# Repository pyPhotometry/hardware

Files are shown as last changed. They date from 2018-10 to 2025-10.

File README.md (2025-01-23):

# pyPhotometry Hardware

This repository contains design files for pyPhometry hardware.  For more information see: https://pyphotometry.readthedocs.io/en/latest/user-guide/hardware/

The repository contains the following devices:

## Acquisition board v1.0

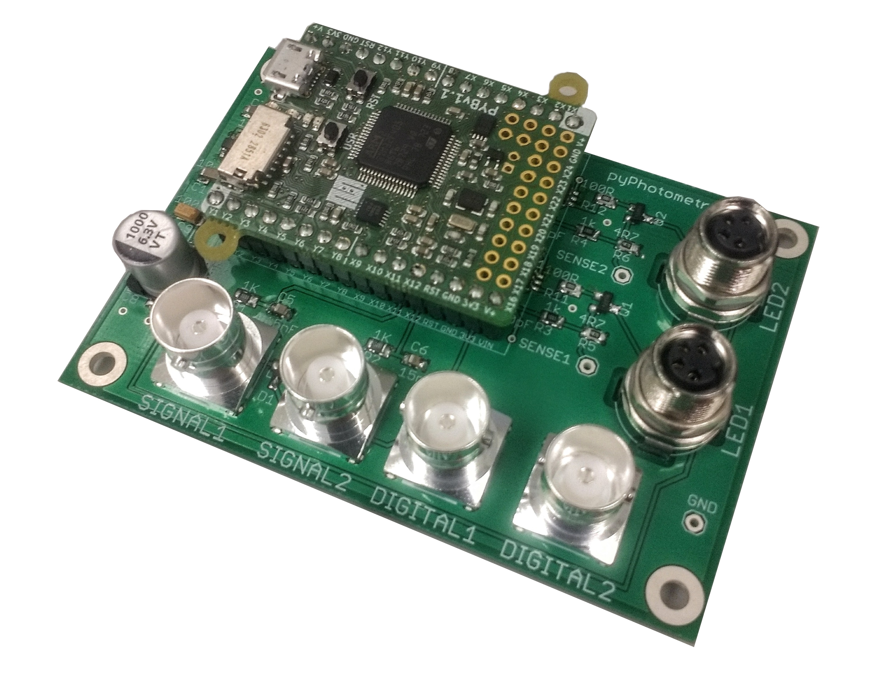
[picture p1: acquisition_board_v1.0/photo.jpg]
board_v1.0


The original version of the acquisition board as detailed in the [pyPhotometry manuscript](https://www.nature.com/articles/s41598-019-39724-y), featuring:

-  2 analog inputs (0-3.3V) for photoreceiver signals.
- 2 Digital inputs for registering behavioural events or sync pulses.
- 2 LED driver outputs with 0-100mA adjustable current output.

## Acquisition board v2.0

board_v2.0

An updated version of the acquisition board with the following improvements from version 1.0:

- Increased maximum current of 300mA from the two LED driver outputs.
- 2 additional LED control outputs for triggering external LED drivers that require a voltage control signal (0-3.3V) , allowing the board to be used with optical hardware like the Doric Gen3 minicubes which have integrated LED drivers.  The signals output on the two LED control outputs are the same signals used to control the on-board LED drivers, so it is not possible to independently use the LED control outputs and the LED driver outputs at the same time.
- Reduced artefacts on analog input signals caused by saturation (i.e. voltage exceeding 3.3V) on the other analog input.
- Additional Picoblade connector providing access to 3 pyboard pins including I2C serial communication.  

## Acquisition board case

board_v2.0

A plastic case compatible both v1.0 and v2.0 acquisition boards.

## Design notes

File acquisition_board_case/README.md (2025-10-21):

# Acquisition board case



Plastic case compatible with both version v1 and v2 acquisition boards.  The repository contains the Fusion 360 design file (.f3z) and an stl file for 3D printing.

### Assembly:

1. 3D print the file `case_body.stl` using selective laser sintering (SLS) in Nylon PA12.

2. Insert thread inserts into body using gentle pressure with soldering iron set to 220 centigrade.  

   The 4 thread inserts on the bottom of the case are optional but allow the case to be mounted using M3 screws (hole spacing 60x50mm).

3. Position board in case and attach with M3 screws.

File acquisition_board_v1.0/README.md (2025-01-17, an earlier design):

# Acquisition board v1.0



The original pyPhotometry acquisition board as detailed in the manuscript, featuring two analog inputs for photoreceiver signal (0-3.3v), two digital inputs, and two LED drivers with 0-100mA adjustable output.

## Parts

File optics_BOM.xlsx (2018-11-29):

Name | Quantity | Part | Supplier
Photoreciever | 2 | Newport 2151 with lensed FC adapter | Doric
465nm LED | 1 | CLED_465 | Doric
560nm LED | 1 | CLED_560 | Doric
Minicube | 1 | FMC5_E1(450-490)_F1(500-540)_E2(550-580)_F2(600-680)_S | Doric
Fiber patchcord: LED - Minicube | 2 | MFP_200/220/LWMJ-0.48_0.3m_FCM-FCM | Doric
Fiber patchcord: Minicube - Photoreciever | 2 | MFP_600/630/LWMJ-0.48_0.3m_FCM-FCM | Doric
Fiber patchcord: Rotary-sample | 1 | MFP_200/220/900-0.48_1m_FCM-MF1.25 | Doric
Pigtailed rotary joint | 1 | FRJ_1x1_PT_200/230/LWMJ-0.48_1m_FCM_0.2m_FCM | Doric
FC-FC adapter | 1 | ADAPTER_FC style 2 | Doric
Optical breadboard 150x300mm metric | 1 | MB1530F/M | Thorlabs
M6 - M3 thread adapter | 4 | MSA6/M | Thorlabs
Clamp for minicube | 1 | CL3/M Compact Variable Height Clamp, M6 Tapped | Thorlabs
Clamp for photodetector | 2 | MSC2 Clamping Fork for 1/4"-20 (M6) Cap Screw | Thorlabs
Pillar for photodetector | 2 | TRP14/M Ø12 mm Pedestal Pillar Post | Thorlabs
M6 screw 12mm | 4 | SH6MS12 | Thorlabs
USB A - micro B cable 1.8m | 1 | 121-3251 | RS
BNC cable 0.3m: Photoreciever to acquisition board | 2 | 886-0706 | RS
M3 screw 10mm | 4 | 660-4636 | RS
M3 spacer 3mm | 4 | 161-3676 | RS
M6 x 45mm | 2 | 468-0133 | RS

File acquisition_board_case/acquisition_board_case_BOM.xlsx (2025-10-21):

Part | Quantity | RS part number | Notes
case_body | 1 | - | SLS 3D print in Nylon PA12
M3 thread insert | 8 | 278-534
M3 6mm button head screw | 4 | 822-9155

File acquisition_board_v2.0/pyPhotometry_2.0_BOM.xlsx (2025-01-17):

Part | Value | Device | Package | Description | MF | MPN | OC_FARNELL
SIGNAL1 |  | - | - | BNC connector | TE CONNECTIVITY | 1-1337445-0 | 1205964
SIGNAL2 |  | - | - | BNC connector | TE CONNECTIVITY | 1-1337445-0 | 1205964
DIGITAL1 |  | - | - | BNC connector | TE CONNECTIVITY | 1-1337445-0 | 1205964
DIGITAL2 |  | - | - | BNC connector | TE CONNECTIVITY | 1-1337445-0 | 1205964
LED1CON |  | - | - | BNC connector | TE CONNECTIVITY | 1-1337445-0 | 1205964
LED2CON |  | - | - | BNC connector | TE CONNECTIVITY | 1-1337445-0 | 1205964
LED1 | - | - | - | M8 connector | TE CONNECTIVITY | T4041037041-000 | 2817801
LED2 | - | - | - | M8 connector | TE CONNECTIVITY | T4041037041-000 | 2817801
PICOBLADE_CON | - | - | - | Picoblade connector | Molex | 53261-0571 | 1125360
IC1 | - | OPA197 | SOT23-5 | Op amp | Texas Instruments | OPA197IDBVT | 2545356
IC2 | - | OPA197 | SOT23-5 | Op amp | Texas Instruments | OPA197IDBVT | 2545356
IC3 | - | MIC2004-0.5YM5 | SOT23-5 | Current limiting switch | Microchip | MIC2004-0.5YM5-TR | 2509877
IC4 |  | MCP1700T-3302E/TT | SOT23-3 | Voltage regulator | Microchip | MCP1700T-3302E/TT | 1296592
C1 | 100nF | - | 0603 | Capacitor | Generic | GPC0603104
C2 | 100nF | - | 0603 | Capacitor | Generic | GPC0603104
C3 | 100pF | - | 0603 | Capacitor | Generic | GPC0603101
C4 | 100pF | - | 0603 | Capacitor | Generic | GPC0603101
C5 | 15nF | - | 0603 | Capacitor | Generic | GPC0603153
C6 | 15nF | - | 0603 | Capacitor | Generic | GPC0603153
C7 | 1uF | - | 0603 | Capacitor | Generic | GPC0603105
C8 | 1uF | - | 0603 | Capacitor | Generic | GPC0603105
C9 | 1000uF | - | - | Capacitor | MULTICOMP | MCVVT6R3M102FB3 | 2611416
C10 | 1000uF | - | - | Capacitor | MULTICOMP | MCVVT6R3M102FB3 | 2611416
C11 | 100uF | - | 1206 | Capacitor | KEMET | T490A107M006ATE500 | 2688577
C12 | 10uF | - | 1206 | Capacitor | Generic | GPC1206106
D1 | - | - | - | Schottky Diode | STMICROELECTRONICS | BAR43CFILM | 9801383
D2 | - | - | - | Schottky Diode | STMICROELECTRONICS | BAR43AFILM | 1611382
Q1 | - | - | SOT23 | Mosfet | Diodes Inc | DMG2302UK-7 | 3127315
Q2 | - | - | SOT23 | Mosfet | Diodes Inc | DMG2302UK-7 | 3127315
R1 | 1K | - | 0603 | Resistor | Generic | GPR06031K
R2 | 1K | - | 0603 | Resistor | Generic | GPR06031K
R3 | 1K | - | 0603 | Resistor | Generic | GPR06031K
R4 | 1K | - | 0603 | Resistor | Generic | GPR06031K
R5 | 2R | - | 0603 | Resistor | Generic | GPR06032R
R6 | 2R | - | 0603 | Resistor | Generic | GPR06032R
R7 | 20K | - | 0603 | Resistor | Generic | GPR060320K
R8 | 20K | - | 0603 | Resistor | Generic | GPR060320K
R9 | 82K | - | 0603 | Resistor | Generic | GPR060382K
R10 | 82K | - | 0603 | Resistor | Generic | GPR060382K
R11 | 100R | - | 0603 | Resistor | Generic | GPR0603100R
R12 | 100R | - | 0603 | Resistor | Generic | GPR0603100R
R13 | 100R | - | 0603 | Resistor | Generic | GPR0603100R
R14 | 100R | - | 0603 | Resistor | Generic | GPR0603100R
R15 | 100R | - | 0603 | Resistor | Generic | GPR0603100R
R16 | 100R | - | 0603 | Resistor | Generic | GPR0603100R
R17 | 100R | - | 0603 | Resistor | Generic | GPR0603100R
R18 | 100R | - | 0603 | Resistor | Generic | GPR0603100R
R19 | 4M7 | - | 0603 | Resistor | Generic | GPR06034M7
R20 | 4M7 | - | 0603 | Resistor | Generic | GPR06034M7
PYBOARD_CON_1 |  | - | - | 1x16 receptacle | SAMTEC | CES-116-01-T-S | 1667522
PYBOARD_CON_2 |  | - | - | 1x16 receptacle | SAMTEC | CES-116-01-T-S | 1667522
PYBOARD_CON_3 |  | - | - | 1x16 header | SAMTEC | TSW-116-06-T-S | 2035403
PYBOARD_CON_4 |  | - | - | 1x16 header | SAMTEC | TSW-116-06-T-S | 2035403
PYBOARD |  | PYBOARD v1.1 | - | PYBOARD v1.1 | https://micropython.org/store | PYBv1.1 | -
Licensed under the TAPR Open Hardware License (www.tapr.org/OHL)
Copyright 2024 Thomas Akam

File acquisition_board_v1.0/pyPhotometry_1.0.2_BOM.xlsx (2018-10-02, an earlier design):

Part | Value | Device | Package | Description | MF | MPN | OC_FARNELL
SIGNAL1 |  | - | - | BNC connector | TE CONNECTIVITY | 1-1337445-0 | 1205964
SIGNAL2 |  | - | - | BNC connector | TE CONNECTIVITY | 1-1337445-0 | 1205964
DIGITAL1 |  | - | - | BNC connector | TE CONNECTIVITY | 1-1337445-0 | 1205964
DIGITAL2 |  | - | - | BNC connector | TE CONNECTIVITY | 1-1337445-0 | 1205964
LED1 | - | - | - | M8 connector | TE CONNECTIVITY | T4041037041-000 | 2817801
LED2 | - | - | - | M8 connector | TE CONNECTIVITY | T4041037041-000 | 2817801
IC1 | - | OPA197 | SOT23-5 | Op amp | Texas Instruments | OPA197IDBVT | 2545356
IC2 | - | OPA197 | SOT23-5 | Op amp | Texas Instruments | OPA197IDBVT | 2545356
IC3 | - | MIC2004-0.5YM5 | SOT23-5 | Current limiting switch | Microchip | MIC2004-0.5YM5-TR | 2509877
C1 | 100nF | - | 0805 | Capacitor | MULTICOMP | MC0805B104K500CT | 1759265
C2 | 100nF | - | 0805 | Capacitor | MULTICOMP | MC0805B104K500CT | 1759265
C3 | 100pF | - | 0805 | Capacitor | MULTICOMP | MC0805B101K500CT | 2627475
C4 | 100pF | - | 0805 | Capacitor | MULTICOMP | MC0805B101K500CT | 2627475
C5 | 15nF | - | 0805 | Capacitor | MULTICOMP | MC0805B153K500CT | 1759249
C6 | 15nF | - | 0805 | Capacitor | MULTICOMP | MC0805B153K500CT | 1759249
C7 | 1uF | - | 0805 | Capacitor | MULTICOMP | MC0805X105K160CT | 2320855
C8 | 1000uF | - | - | Capacitor | MULTICOMP | MCVVT6R3M102FB3 | 2611416
C9 | 100uF | - | 1206 | Capacitor | KEMET | T490A107M006ATE500 | 2688577
C10 | 10uF | - | 0805 | Capacitor | MULTICOMP | MC0805B106K6R3CT | 2320851
D1 | - | - | - | Schottky Diode | STMICROELECTRONICS | BAR43CFILM | 9801383
Q1 | - | - | SOT23 | Mosfet | INFINEON | IRLML2803GTRPBF | 2726008
Q2 | - | - | SOT23 | Mosfet | INFINEON | IRLML2803GTRPBF | 2726008
R1 | 1K | - | 0805 | Resistor 0805 | MULTICOMP | MC01W080551K | 9333711
R2 | 1K | - | 0805 | Resistor 0805 | MULTICOMP | MC01W080551K | 9333711
R3 | 1K | - | 0805 | Resistor 0805 | MULTICOMP | MC01W080551K | 9333711
R4 | 1K | - | 0805 | Resistor 0805 | MULTICOMP | MC01W080551K | 9333711
R5 | 4R7 | - | 0805 | Resistor 0805 | MULTICOMP | MCMR08W4R70FTL | 2073599
R6 | 4R7 | - | 0805 | Resistor 0805 | MULTICOMP | MCMR08W4R70FTL | 2073599
R7 | 20K | - | 0805 | Resistor 0805 | MULTICOMP | MCPWR05FTEW2002 | 1887316
R8 | 20K | - | 0805 | Resistor 0805 | MULTICOMP | MCPWR05FTEW2002 | 1887316
R9 | 100K | - | 0805 | Resistor 0805 | MULTICOMP | MCWR08X1003FTL | 2447551
R10 | 100K | - | 0805 | Resistor 0805 | MULTICOMP | MCWR08X1003FTL | 2447551
R11 | 100R | - | 0805 | Resistor 0805 | MULTICOMP | MCWR08X1000FTL | 2447552
R12 | 100R | - | 0805 | Resistor 0805 | MULTICOMP | MCWR08X1000FTL | 2447552
R13 | 4M7 | - | 0805 | Resistor 0805 | MULTICOMP | MCWR08W4704FTL | 2447676
R14 | 4M7 | - | 0805 | Resistor 0805 | MULTICOMP | MCWR08W4704FTL | 2447676
PYBOARD_CON_1 |  | - | - | 1x16 receptacle | SAMTEC | CES-116-01-T-S | 1667522
PYBOARD_CON_2 |  | - | - | 1x16 receptacle | SAMTEC | CES-116-01-T-S | 1667522
PYBOARD_CON_3 |  | - | - | 1x16 header | SAMTEC | TSW-116-06-T-S | 2035403
PYBOARD_CON_4 |  | - | - | 1x16 header | SAMTEC | TSW-116-06-T-S | 2035403
PYBOARD |  | PYBOARD v1.1 | - | PYBOARD v1.1 | https://micropython.org/store | PYBv1.1 | -
Licensed under the TAPR Open Hardware License (www.tapr.org/OHL)
Copyright 2018 Thomas Akam

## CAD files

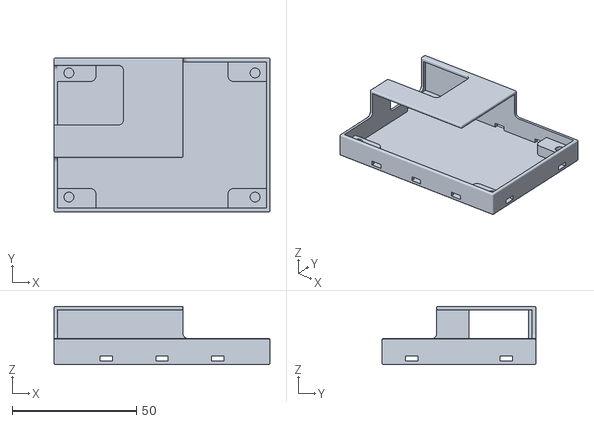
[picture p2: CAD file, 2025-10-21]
acquisition_board_case/case_body.stl
87.0 x 62.0 x 23.5

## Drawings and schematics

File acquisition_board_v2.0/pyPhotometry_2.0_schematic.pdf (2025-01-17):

A

A

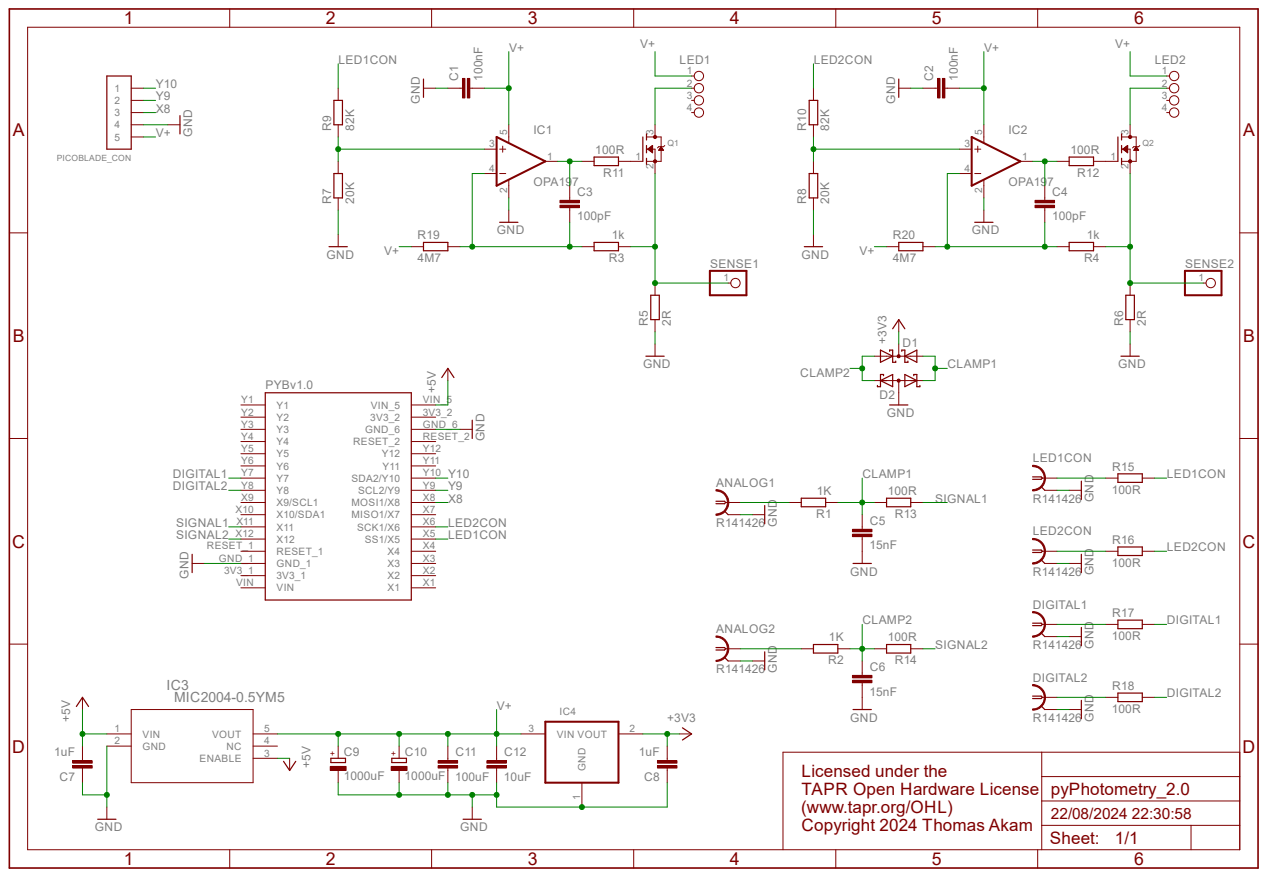
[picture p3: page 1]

Licensed under the TAPR Open Hardware License (www.tapr.org/OHL) Copyright 2024 Thomas Akam

Sheet: 1/1

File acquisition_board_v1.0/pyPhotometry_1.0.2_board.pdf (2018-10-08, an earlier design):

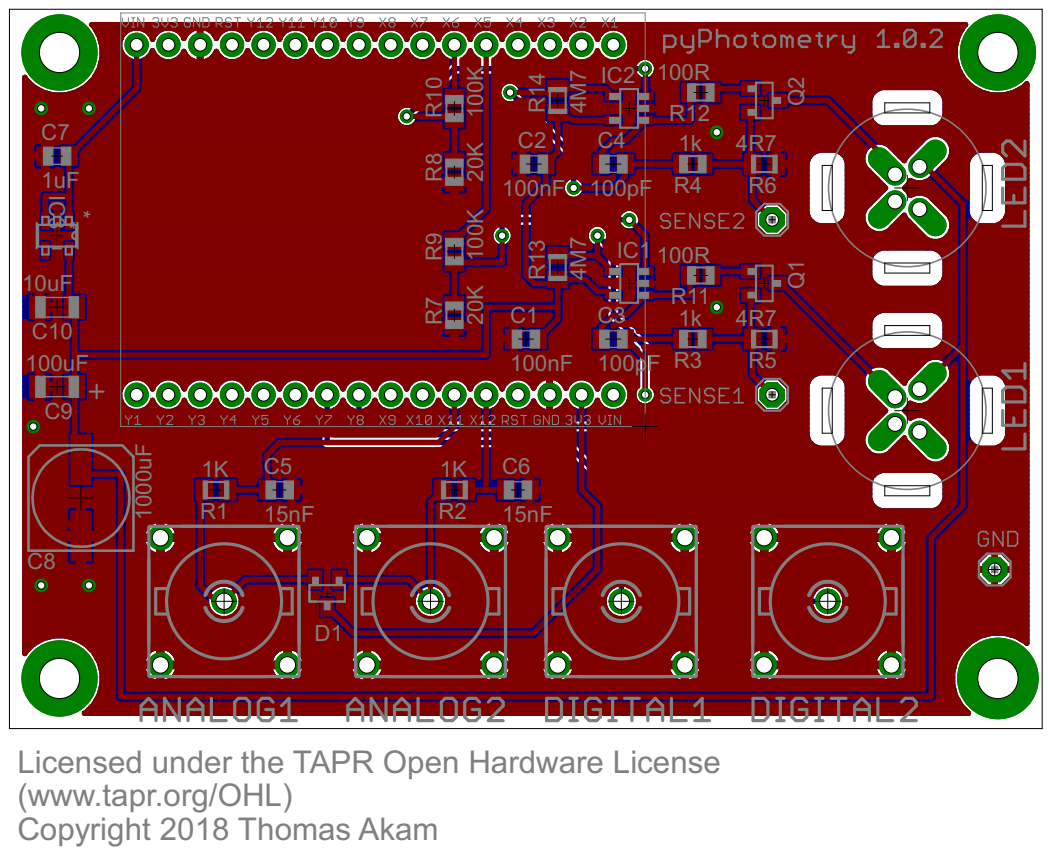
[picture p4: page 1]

* Licensed under the TAPR Open Hardware License

C10
100uF | 100nF 100pF

(www.tapr.org/OHL)
Copyright 2018 Thomas Akam

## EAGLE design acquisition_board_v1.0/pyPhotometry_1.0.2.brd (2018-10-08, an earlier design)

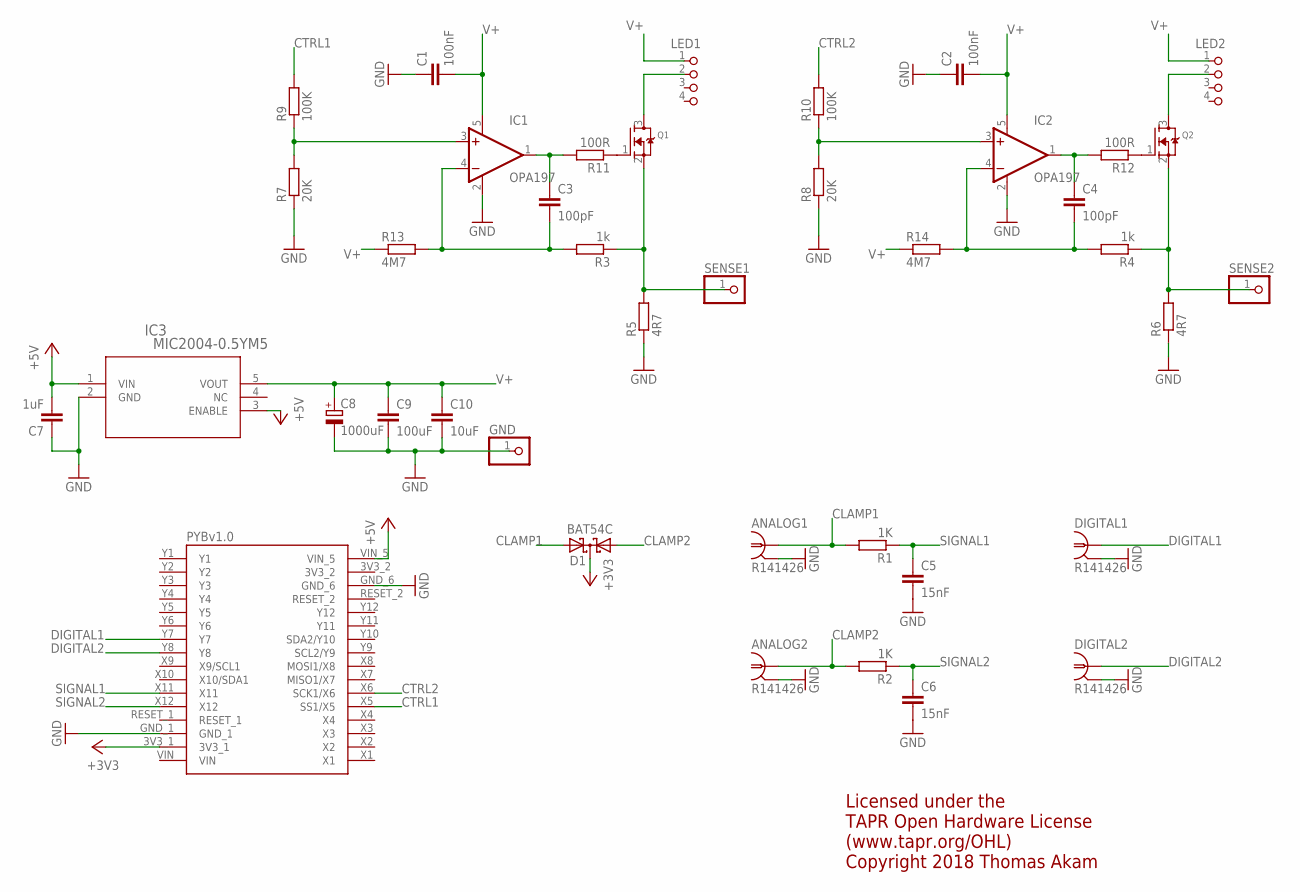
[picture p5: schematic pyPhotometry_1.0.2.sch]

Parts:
ANALOG1, ANALOG2: R141426
C1, C2: 100nF; C0805
C3, C4: 100pF; C0805
C5, C6: 15nF; C0805
C7: 1uF; C0805
C8: 1000uF; 153CLV-0807
C9: 100uF; C1206
C10: 10uF; C1206
D1: BAT54C; SOT23
DIGITAL1, DIGITAL2: R141426
GND: PINHD-1X1; 1X01
IC1, IC2: OPA197; SOT23-5
IC3: MIC2004-0.5YM5; SOT-23-5_M5
LED1, LED2: M8-4
Q1, Q2: MOSFET-NREFLOW; SOT23
R1, R2: 1K; M0805
R3, R4: 1k; R0805
R5, R6: 4R7; M0805
R7, R8: 20K; R0805
R9, R10: 100K; R0805
R11, R12: 100R; R0805
R13, R14: 4M7; M0805
SENSE1, SENSE2: PINHD-1X1; 1X01
U$1: PYBOARD-REDUCED-3

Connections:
+3V3: D1.3 (CC), U$1.3V3_1
+5V: C7.2, IC3.1 (VIN), IC3.3 (ENABLE), U$1.VIN_5
CLAMP1: ANALOG1.1, D1.2 (A2), R1.2
CLAMP2: ANALOG2.1, D1.1 (A1), R2.2
CTRL1: R9.2, U$1.X5 (SS1/X5)
CTRL2: R10.2, U$1.X6 (SCK1/X6)
DIGITAL1: DIGITAL1.1, U$1.Y7
DIGITAL2: DIGITAL2.1, U$1.Y8
GND: ANALOG1.2 (GND), ANALOG1.3 (GND), ANALOG1.4 (GND), ANALOG1.5 (GND), ANALOG2.2 (GND), ANALOG2.3 (GND), ANALOG2.4 (GND), ANALOG2.5 (GND), C1.1, C2.1, C5.2, C6.2, C7.1, C8.-, C9.2, C10.2, DIGITAL1.2 (GND), DIGITAL1.3 (GND), DIGITAL1.4 (GND), DIGITAL1.5 (GND), DIGITAL2.2 (GND), DIGITAL2.3 (GND), DIGITAL2.4 (GND), DIGITAL2.5 (GND), GND.1, IC1.2 (V-), IC2.2 (V-), IC3.2 (GND), R5.1, R6.1, R7.1, R8.1, U$1.GND_1, U$1.GND_6
unnamed: C3.1, IC1.1 (OUT), R11.2
unnamed: C3.2, IC1.4 (-IN), R3.2, R13.2
unnamed: IC1.3 (+IN), R7.2, R9.1
unnamed: Q1.1 (G), R11.1
unnamed: LED1.2, Q1.3 (D)
unnamed: Q1.2 (S), R3.1, R5.2, SENSE1.1
unnamed: C4.1, IC2.1 (OUT), R12.2
unnamed: Q2.2 (S), R4.1, R6.2, SENSE2.1
unnamed: C4.2, IC2.4 (-IN), R4.2, R14.2
unnamed: IC2.3 (+IN), R8.2, R10.1
unnamed: Q2.1 (G), R12.1
unnamed: LED2.2, Q2.3 (D)
SIGNAL1: C5.1, R1.1, U$1.X11
SIGNAL2: C6.1, R2.1, U$1.X12
V+: C1.2, C2.2, C8.+, C9.1, C10.1, IC1.5 (V+), IC2.5 (V+), IC3.5 (VOUT), LED1.1, LED2.1, R13.1, R14.1

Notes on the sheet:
Licensed under the TAPR Open Hardware License (www.tapr.org/OHL) Copyright 2018 Thomas Akam

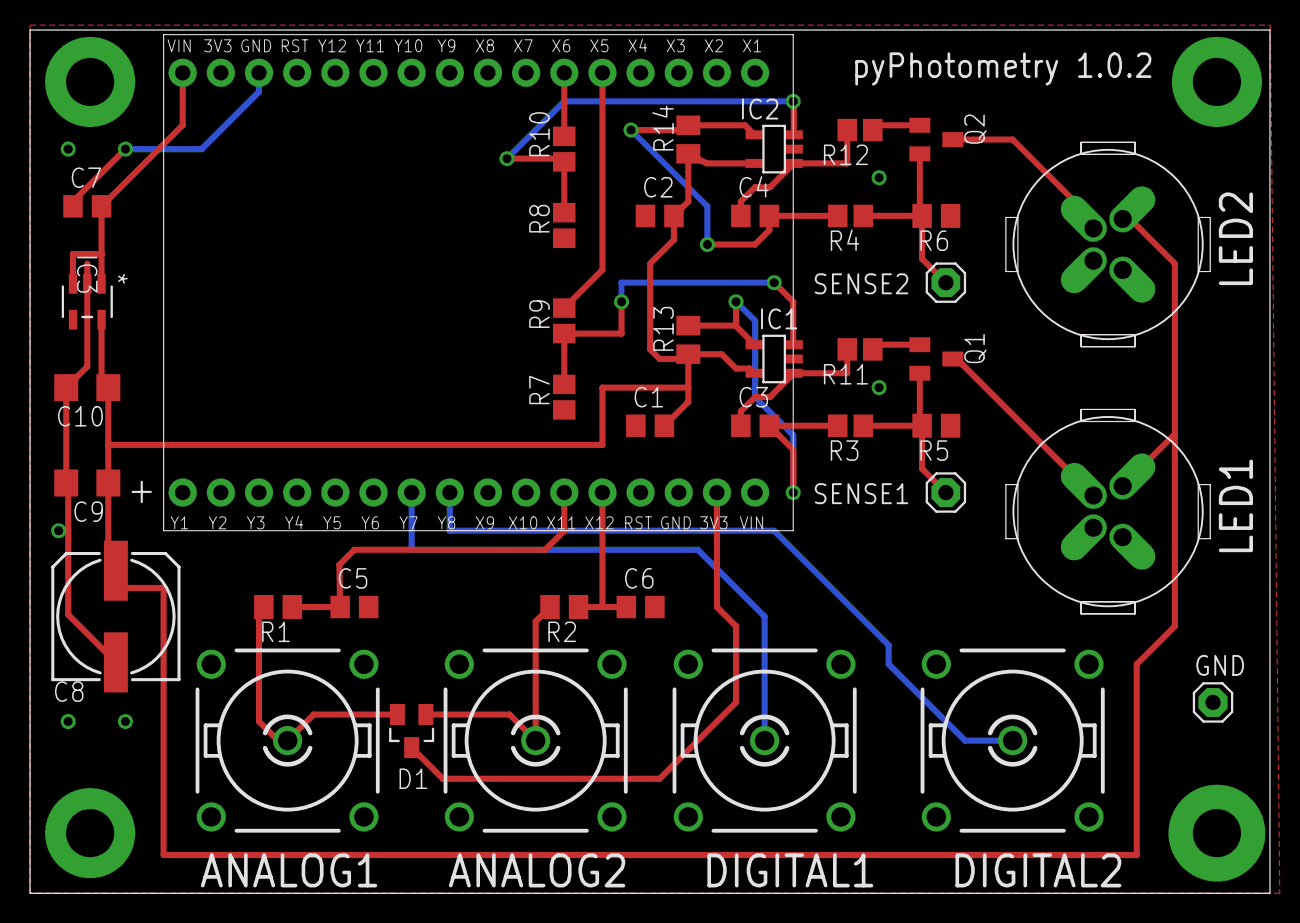
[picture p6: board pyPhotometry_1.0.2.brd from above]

Board: 2 copper layers, 82.5 x 57.5 mm, 40 parts (0 on the bottom side), 24 nets.

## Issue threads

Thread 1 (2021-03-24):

### ISSUE TITLE
PCB and SMD soldering

### ISSUE THREAD

**Issue by amchagas** [pyPhotometry/hardware#1]
Hi Thomas,

We are going to implement one unit of PyPhotometry here at Sussex, and after taking a look at the hardware documentation, I was wondering how you soldered the boards? 
Did you use a stencil for placing the SMD components or did you solder them by hand? If you used a stencil, are the files to generate one available with the gerber zip file?

Thanks!

**Comment by ThomasAkam** [comment]
Hi Andre,

I hand soldered the prototype boards so did not make a stencil, but I think the file needed to generate a stencil is file  _pyPhotometry_1.0.2.gtp_ file in the gerber zip.

**Comment by amchagas** [comment]
Thanks!

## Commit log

2018-10-02 Initial commit.
    [pyPhotometry_1.0.2.brd, pyPhotometry_1.0.2.sch, pyPhotometry_1.0.2_BOM.xlsx]
2018-10-03 - Moved acquisition board files to seperate folder.
    - Added optics_BOM
    [optics_BOM.xlsx, pyPhotometry_1.0.2.brd, pyPhotometry_1.0.2.sch, pyPhotometry_1.0.2_BOM.xlsx]
2018-10-08 - Increaced slot width for M8 connectors for compatibility with OEPS PCB fabrication.
    - Added PDF of board.
    [pyPhotometry_1.0.2.brd, pyPhotometry_1.0.2.sch]
2018-10-17 - Fixed incorrect NA on rotary-sample fiber in optics BOM.
    [optics_BOM.xlsx]
2018-11-06 - Fixed part number for minicube clamp in optic BOM.
    [optics_BOM.xlsx]
2018-11-29 - Optics_BOM: Changed fiber connecting LEDs to minicube from 0.22 to 0.48NA.
    [optics_BOM.xlsx]
2024-08-21 Added version number to acqusition board folder name.
    [pyPhotometry_1.0.2.GBL, pyPhotometry_1.0.2.GBO, pyPhotometry_1.0.2.GBS, pyPhotometry_1.0.2.GTL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]
2025-01-17 Added acqusition board v2.0 and acquisition board case.
    [acquisition_board_case_BOM.xlsx, case_body.stl, pyPhotometry_1.0.2.GBL, pyPhotometry_1.0.2.GBO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]
2025-01-17 Replaced spaces with underscores in folder names
    [acquisition_board_case_BOM.xlsx, case_body.stl, pyPhotometry_1.0.2.brd, pyPhotometry_1.0.2.sch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]
2025-01-17 Added pdf of v2.0 board schematic.
2025-01-23 Edited readmes for v2.0 board.
2025-01-30 Added gerber files for the acqusition boards
    [pyPhotometry_1.0.2.GBL, pyPhotometry_1.0.2.GBO, pyPhotometry_1.0.2.GBS, pyPhotometry_1.0.2.GTL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]
2025-10-21 Added threaded mounting holes to bottom of case.
    [acquisition_board_case_BOM.xlsx, case_body.stl]
2025-11-25 Added version of case for use with OEPS pyboard.
